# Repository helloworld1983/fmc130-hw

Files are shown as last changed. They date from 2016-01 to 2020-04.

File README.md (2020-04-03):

# FMC ADC 130M 16B 4CHA

## Project description

One of the most important goals in every light source is to achieve
orbit stability for the electron beam within the required specifications
for the stability of the photon beam in the experimental stations.
Several technical challenges make the task of achieving sub-micrometer
stability really demanding in terms of mechanical and electrical
engineering. Fast feedback systems are employed to dump orbit
distortions through accurate measurements of the beam positions, fast
computation of the corrections and actuation back to the beam through
fast power supplies and steering magnets. To realize this task in the
\*SIRIUS\*http://www.lnls.br, the new brazilian synchrotron light
source, a digital platform to measure the beam position is required.
Inside this plattaform a key part is the analog to digital conversion.
This text will describe the main specification for an FMC
Analog-to-digital conversion board.

There are several commercial off-the-shelf digitizers covering a wide
range of speed, bandwidth and resolution, but there is no board that
cover all features required for the LNLS
design.

-----



*FMC ADC 130M 16B 4CHA production board** - ([Top
view](https://www.ohwr.org/project/fmc-adc-130m-16b-4cha/uploads/23f18a16ba281e2f93acb31782c0db42/top_r.jpg), [Bottom
view](https://www.ohwr.org/project/fmc-adc-130m-16b-4cha/uploads/616fc42ba8aeb56efde3af8f24af65d3/bot_r.jpg), [Front
view](https://www.ohwr.org/project/fmc-adc-130m-16b-4cha/uploads/30c50ed58559d64d9c38bfc512450c89/fmc_bot.jpg) )

## Functional specifications

- VITA 57.1-2010 compliant
- Four Channel 16 bit 130 MSPS ADC. Required ADC: LTC2208IUP
- Internal ADC clock circuit: Phase locked to the external reference clock input with fine frequency tuning capability. See specific section. Hold mode in case of loss of external reference is a desirable feature.
- Internal high frequency PLL oscillator output with amplitude control and locked to external reference.
- External ADC clock input (50 MHz up to 130 MHz, 0 dBm typ.)
- External reference clock input: (0.5 MHz - 20 MHz digital signal, 0 dBm typ.)
- External digital Trigger input
- External digital Trigger output
-----
## Detailed project information
Block diagram

|Date|Activity|
|----|----|
|01/10/2011|First sudies about necessities|
|27/11/2011|FMC standard choosed|
|05/03/2012|Project started at OHWR|
|15/03/2012|ADC choosed|
|26/03/2012|power dissipation solutions studied|
|04/05/2012|Specification document V1.0 done|
|22/05/2012|Start of block diagram design: clock schemes, PS, input stage,FMC interface,etc|
|01/08/2012|Start collaboration with WUT/Creotech for boards design (130 and 250 MSPS versions)|
|22/10/2012|Start schematics and discussions with WUT/Creotech|
|03/12/2012|Decision of layout unification for reuse of heatsink in both boards|
|06/12/2012|Start of design modification, mechanical unification with FMC ADC 250M version|
|19/12/2012|Layout ready for review|
|21/12/2012|Fast review send from LNLS to WUT/Creotech|
|12/02/2013|Pre-assembled boards received by WUT/Creotech|
|14/02/2013|Start basic tests|
|26/04/2013|FMC ready, tested and assembled|
|30/09/2014|Available commercially|

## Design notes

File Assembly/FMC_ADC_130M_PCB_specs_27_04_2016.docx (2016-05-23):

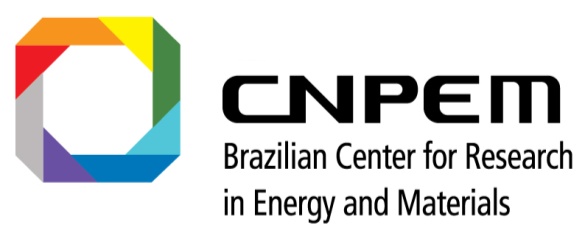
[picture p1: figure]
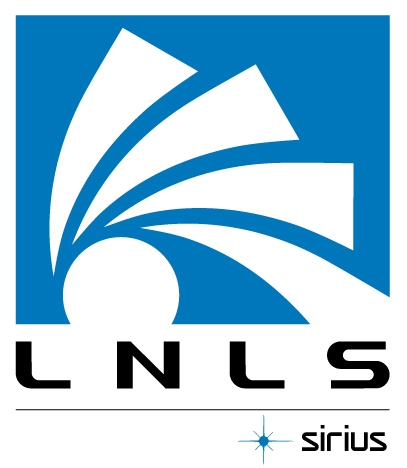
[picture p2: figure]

Manufacturing specifications for the FMC_ADC_130M hardware

April 2016

Beam Diagnostics Group (DIG)

BLANK PAGE

# PCB Fabrication Specification

Design references
Name | FMC_ADC_130M | Date: | 04/27/2015
File name
Designers | Rafael Antonio Baron | Fernando Cambauva SantAnna
E-mail | | fernando.santanna@lnls.br
Fone | | +55 19 3512-5071
Cel | | +55 16 99206-8595

Mechanical characteristics
External size (mm) | 77 x 69 mm
Thickness (mm) | 1.4 mm
Layers | 8
Min track width (mm/mils) | 3mils
Min Hole size (mm/mils) | 7.8mils
Laminate | FR-4 – TG150
Pre-preg | FR-4 – TG150

Finish Copper
External layers (µm) | 35 µm
Holes walls (µm) | 25 µm
Internal Layers-Planes (µm) | 35 µm
Internal Layers-Signals (µm) | 35 µm

Board finishing requirements
Mask Solder color | Red for prototype and Blue for production
Silkscreen on top layer (color) | White
Silkscreen on bottom layer (color) | White
Surface Finishing | ENIG – Electroless Nickel / Immersion Gold according to IPC-4552
Thickness | Ni: 3 µm min, 6 µm máx. Au: 0.05 µm min, 0.125 µm máx

Additional Information
Impedance test | No
Packaging requirements | No
Documentation to be delivered | No
Additional control quality requirements | No

| | Board Stackup Information
| Name: | | | Laminate/pre-preg | Thickness (mm/mils)
Layer 1 | Top Layer | | RF signals
Layer 2 | GND1 | | RF Ground Plane | FR-4 | 0.11mm
Layer 3 | L3 | | Digital signals | FR-4 | 0.1mm
Layer 4 | GND2 | | RF Ground Plane + Digital Ground plane | FR-4 | 0.29mm
Layer 5 | L5 | | Digital signals | FR-4 | 0.1mm
Layer 6 | GND3 | | RF Ground Plane + Digital Ground plane | FR-4 | 0.29mm
Layer 7 | Power | | Power | FR-4 | 0.1mm
Layer 8 | Bottom Layer | | Digital signals | FR-4 | 0.11mm
Total | | | | Total | 1.481 mm

Centro Nacional de Pesquisa em Energia e Materiais (CNPEM) Laboratório Nacional de Luz Síncrotron (LNLS) Rua Giuseppe Maximo Scolfaro, 10000, Polo II de Alta Tecnologia Campinas, São Paulo, Brazil CEP 13083-970 – Caixa Postal 6192

Last update: 27 April 2016 - 14:16 4

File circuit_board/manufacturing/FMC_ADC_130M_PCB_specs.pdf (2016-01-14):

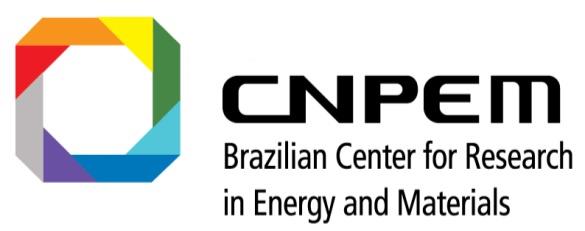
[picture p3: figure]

### Centro Nacional de Pesquisa em Energia e Materiais (CNPEM) Laboratório Nacional de Luz Síncrotron (LNLS) Rua Giuseppe Maximo Scolfaro, 10000, Polo II de Alta Tecnologia Campinas, São Paulo, Brazil CEP 13083-970 – Caixa Postal 6192

# Manufacturing specifications for the FMC_ADC_130M hardware

# December 2015

# Beam Diagnostics Group (DIG)

BLANK PAGE

Last update: 11 December 2015 - 14:26 | 3

## PCB Fabrication Specification

## Design references

Name | FMC_ADC_130M | Date: | 1/12/2015
File name
Designers | Rafael Antonio Baron | Fernando Cambauva SantAnna
E-mail | | fernando.santanna@lnls.br
Fone | | +55 19 3512-5071
Cel | | +55 19 99206-8595

## Mechanical characteristics

External size (mm) | 77 x 69 mm
Thickness (mm) | 1.4 mm
Multilayers | 6 layers
Min track width (mm/mils) | 3mils
Min Hole size (mm/mils)
Laminate | FR-4
Pre-preg | FR-4

## Finish Copper

External layers (µm) | 35 µm
Holes walls (µm) | 25 µm
Internal Layers-Planes (µm) | 35 µm
Internal Layers-Signals (µm) | 35 µm

## Board finishing requirements

Mask Solder color | Red
Silkscreen on top layer (color) | White
Silkscreen on bottom layer (color) | White
Surface Finishing | ENIG – Electroless Nickel / Immersion Gold according to IPC-4552
Thickness | Ni: 3 µm min, 6 µm máx. Au: 0.05 µm min, 0.125 µm máx

## Additional Information

Impedance test | No
Packaging requirements | No
Documentation to be delivered | No
Additional control quality requirements | No

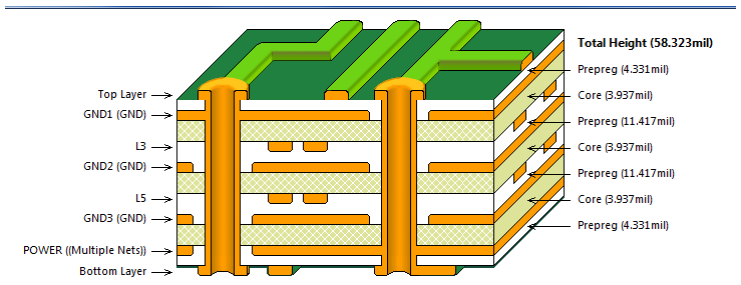
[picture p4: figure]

Last update: 11 December 2015 - 14:26 | 4

## Board Stackup Information

| | Laminate/pre-preg | Thickness (mm/mils)
Layer 1 | RF signals
Layer 2 | RF Ground Plane | FR-4 | 4.3 mils
Layer 3 | Digital signals | FR-4 | 3.9 mils
Layer 4 | RF Ground Plane + Digital Ground plane | FR-4 | 11.4 mils
Layer 5 | Digital signals | FR-4 | 3.9 mils
Layer 6 | Power | FR-4 | 4.3 mils
Total | | | 58 mils = 1.4 mm

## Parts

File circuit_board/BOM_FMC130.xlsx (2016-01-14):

BILL OF MATERIALS
Prj: | FMC - Active | REV.: 6 | Data: | 2015-11-12
QTD | Description | Manufacturer PN | Manufacturer | Designator
98 | CC0201_100NF_6.3V_10%_X5R | 02016D104KAT2A | AVX | C1A, C1B, C1C, C1D, C2A, C2B, C2C, C2D, C10, C14A, C14B, C14C, C14D, C15A, C15B, C15C, C15D, C16A, C16B, C16C, C16D, C17A, C17B, C17C, C17D, C18A, C18B, C18C, C18D, C19A, C19B, C19C, C19D, C20A, C20B, C20C, C20D, C21A, C21B, C21C, C21D, C22A, C22B, C22C, C22D, C23A, C23B, C23C, C23D, C24A, C24B, C24C, C24D, C25A, C25B, C25C, C25D, C26A, C26B, C26C, C26D, C31, C37, C39, C41, C42, C43, C44, C45, C46, C47, C48, C49, C50, C54, C59, C60, C61, C62, C63, C64, C65, C66, C67, C68, C69, C70, C71, C72, C74, C84, C103, C105, C106, C107, C108, C109, C110
4 | CC0402_1.5PF_50V_0.25PF_NP0 | 223886915158 | PHYCOMP | C5A, C5B, C5C, C5D
4 | CC0402_2.2PF_50V_0.25PF_NP0 | 223886915228 | PHYCOMP | C6A, C6B, C6C, C6D
4 | CC0603_2.2UF_16V_10%_X5R | CC0603KRX5R7BB225 | YAGEO | C12A, C12B, C12C, C12D
6 | CC1206_22UF_6.3V_20%_X5R | C1206C226K9PAC | KEMET | C27, C32, C33, C34, C81, C82
13 | CC0805_10UF_16V_10%_X5R | C0805C106K4PAC | KEMET | C28, C29, C36, C38, C51, C75, C76, C85, C86, C88, C95, C99, C100
2 | CAP. CCM SMD 330NF/50V +-10% X7R 0603 | C1608X7R1H334K | TDK | C30, C73
1 | CTE7343-31_100UF_20V_10% | TAJD107K020R | AVX | C35
7 | CC0603_1UF_25V_10%_X7R | GRM188R71E105KA12D | MURATA | C52, C79, C80, C93, C94, C98, C102
1 | CAP. CCM SMD 4,7UF/10V +-10% X5R 0603 | C0603C475K8PACTU | KEMET | C53
2 | CC0603_27NF_25V_10%_X7R | 223891615642 | PHYCOMP | C55, C56
1 | CC0603_10NF_50V_10%_X7R | 223858615636 | PHYCOMP | C57
1 | CAP. CCM SMD 470NF/25V +-20% Z5U 0603 | C1608JB1E474M080AC | TDK | C58
6 | CC0805_47UF_6.3V_20%_X5R | C0805C476M9PACTU | KEMET | C77, C78, C91, C92, C97, C101
1 | CC0402_100PF_50V_5%_NP0 | 223886915101 | PHYCOMP | C96
1 | CC0201_10NF_10V_10%_X5R | 0201ZD103KAT2A | AVX | C104
1 | Serial Diode | BAR66 | INFINEON | D1
4 | 16-Bit, 130Msps ADC | LTC2208IUP#PBF | LINEAR TECHNOLOGY | IC1A, IC1B, IC1C, IC1D
2 | Digital Temperature Sensor and Thermal Watchdog with Two-Wire Interface | LM75AIMM/NOPB | TEXAS INSTRUMENTS | IC2, IC13
1 | 1.2 GHz Clock Distribution IC, PLL Core, Dividers, Delay Adjust, Eight Outputs | AD9510BCPZ | ANALOG DEVICES | IC3
1 | 4 Way-0° 50 OHM 5 to 1000 MHz Power Splitter/Combiner | SCA-4-10+ | MINI-CIRCUITS | IC4
1 | 1.7-5.5V 64K I2C Serial EEPROM | 24AA64T-I/MC | MICROCHIP TECHNOLOGY | IC5
6 | Low Noise (3uVrms), 1A, High Voltage Low-Dropout Linear Regulator | TPS7A4700RGWT | TEXAS INSTRUMENTS | IC6, IC7, IC9, IC10, IC11, IC12
1 | 4.5V-20V To 0.6V-5V, Iout 6A DC/DC low EMI uModule | LTM4606EV#PBF | LINEAR TECHNOLOGY | IC8
1 | 4-BIT DUAL-SUPPLY BUS TRANSCEIVER | SN74AVC4T245PW | TEXAS INSTRUMENTS | IC14
4 | 20-BIT DUAL SUPPLY BUS TRANSCEIVER | SN74AVC20T245ZQLR | TEXAS INSTRUMENTS | IC15A, IC15B, IC15C, IC15D
1 | 2:1 Differential-to-LVDS Multiplexer | ICS854S015CKI-01LF | IDT, Integrated Device Technology Inc | IC16
1 | High Speed Differential Transceiver LVDS/LVTTL | SN65LVDM176DGK | TEXAS INSTRUMENTS | IC17
3 | CONN MMCX JACK R/A 50 OHM PCB | 262105 | AMPHENOL | J1, J2, J10
2 | U.FL | U.FL-R-SMT-1 | HIROSE (HRS) | J3, J4
4 | RF Connector, SMA Right Angle PCB Jack, 50 Ohm | 901-143-4 | AMPHENOL | J5, J6, J7, J8
1 | Connector VITA 57, 400 Male contacts in 10 row | ASP-134488-01 | SAMTEC | J9
5 | Inductor 0402 220ohm±25% | BLM15HB221SN1 | MURATA | L2A, L2B, L2C, L2D,L8
13 | Inductor 0805 220ohm±25% | BLM21PG221SN1D | MURATA | L3, L4A, L4B, L4C, L4D, L6, L7, L12, L13, L14A, L14B, L14C, L14D
5 | MA-COM E-Serie RF 1:1 Transmission Line Ttransformer 4.5-3000MHz | MABA-007159-000000 | MA-COM TECHNOLOGY | L1A, L1B, L1C, L1D,L5
3 | Indutor Choke Coil 2.2uH, 1.4A, 92mR ±20% | ELLVGG2R2N | Panasonic | L9, L10, L15
2 | Tricolor LEDs 1 Cathode Blue, 2 Common Anode, 3 Cathode Red, 4 Cathode Green | HSMF-C113 | AVAGO TECHNOLOGIES | LD1, LD2
1 | Any-Rate I2C Programmable XO Oscillator Si570 Serie 10-215MHZ | Si570BBC000121DG | SILICON LABS | OSC2
3 | Dual NMOS 20V,08.A, 340mR, Vt=0.7V | PMGD280UN | NXP | Q1, Q2, Q5
16 | R0402_5R6_1%_0.0625W_200PPM | RC0402FR-075R6L | YAGEO PHYCOMP | R1A, R1B, R1C, R1D, R2A, R2B, R2C, R2D, R8A, R8B, R8C, R8D, R9A, R9B, R9C, R9D
8 | R0402_33R_1%_0.0625W_100PPM | 232270673309L | YAGEO PHYCOMP | R3A, R3B, R3C, R3D, R6A, R6B, R6C, R6D
11 | R0402_10K_1%_0.0625W_100PPM | 232270671003L | YAGEO PHYCOMP | R4, R5, R10A, R10B, R10C, R10D, R32, R43, R44, R48, R80
2 | R0402_47R_1%_0.0625W_100PPM | RC0402FR-0747RL | YAGEO PHYCOMP | R7, R19
15 | R0402_200R_1%_0.0625W_100PPM | 232270672001L | YAGEO PHYCOMP | R12, R21, R25, R26, R29, R30, R31, R34, R36, R38, R52, R64, R65, R84, R85
5 | R0402_1K_1%_0.0625W_100PPM | 232270671002L | YAGEO PHYCOMP | R13A, R13B, R13C, R13D, R28
4 | R0402_2K_1%_0.0625W_100PPM | 232270672002L | YAGEO PHYCOMP | R14A, R14B, R14C, R14D
9 | R0402_100R_1%_0.0625W_100PPM | 232270671001L | YAGEO PHYCOMP | R16A, R16B, R16C, R16D, R20, R22, R75, R89,R45
12 | R0402_51R_1%_0.0625W_100PPM | 232270675109L | YAGEO PHYCOMP | R17A, R17B, R17C, R17D, R18A, R18B, R18C, R18D, R76A, R76B, R76C, R76D
25 | R0402_0R_JUMPER | 232270591001L | YAGEO PHYCOMP | R23, R27, R35, R37, R39, R40, R42, R62, R63, R66, R67, R68, R69, R70, R71, R72, R73, R77A, R77B, R77C, R77D, R86A, R86B, R86C, R86D
1 | R0402_5K1_1%_0.0625W_100PPM | RC0402FR-075K1L | YAGEO PHYCOMP | R46
1 | R0603_4K12_0.1%_0.063W_10PPM | RN73C1J4K12BTDF | TYCO HOLSWORTHY | R47
4 | R0402_2K2_1%_0.0625W_100PPM | 232270672202L | YAGEO PHYCOMP | R49, R50, R54, R55
1 | R0402_1R_1%_0.0625W_100PPM | RC0402FR-071RL | YAGEO PHYCOMP | R53
1 | R0603_4K7_1%_0.1W_100PPM | NRC06F4701TRF | NIC COMPONENT | R74
2 | R0402_100K_1%_0.0625W_100PPM | 232270671004L | YAGEO PHYCOMP | R78, R79
1 | R1210_49R9_5%_0.5W_200PPM | CRCW121049R9FKEA | Vishay Dale | R87
1 | R0402_4K7_1%_0.0625W_100PPM | 232270674702 | PHYCOMP | R88
4 | 200MHz - 500MHz Ultra Low Profile Sub-Miniature Balanced to Unbalanced Transformer | BD0205F5050A00 | ANAREN MICROWAVE | TR2, TR3, TR4, TR5
1 | 50 Ohm 0.4 To 500MHz RF Transformers | TC1-1+ | MINI-CIRCUITS | TR6

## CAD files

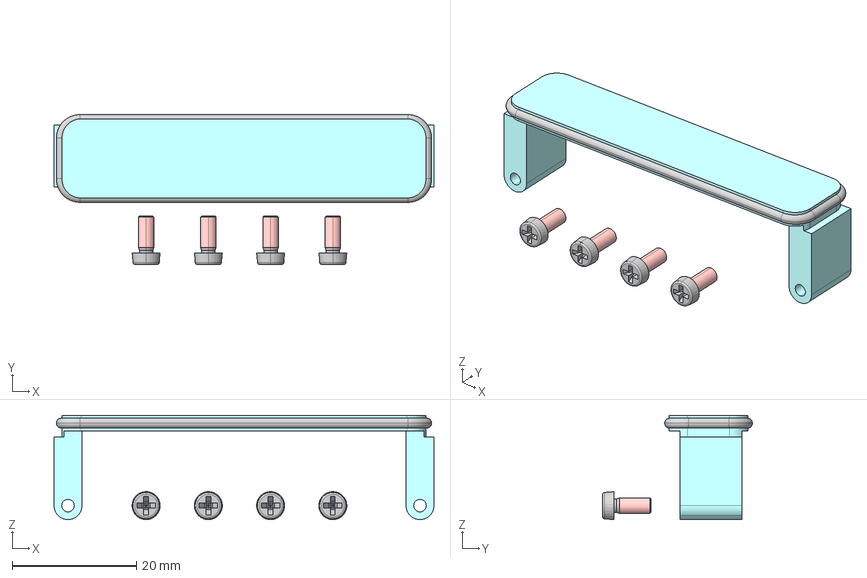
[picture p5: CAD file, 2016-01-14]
mechanical/front panel/21M280-1-3D-STEP.stp
61.0 x 24.1 x 16.8 mm
5325-06_Zylinderschraube_DCH000001699.3 x 4
61-048_EMV_Dichtung_montiert_DCH000054389
21M280_Frontplatte_DCH000054395

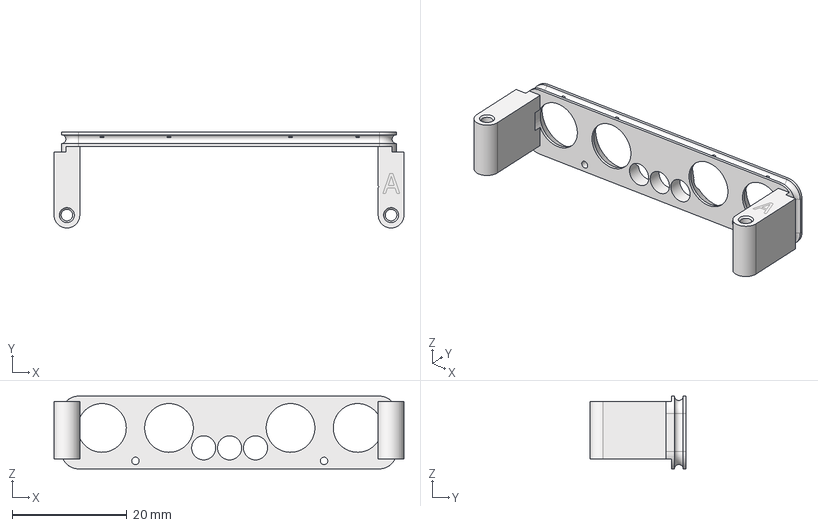
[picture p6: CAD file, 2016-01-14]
mechanical/front panel/Painel FMC v4.stp
61.1 x 16.8 x 12.7 mm

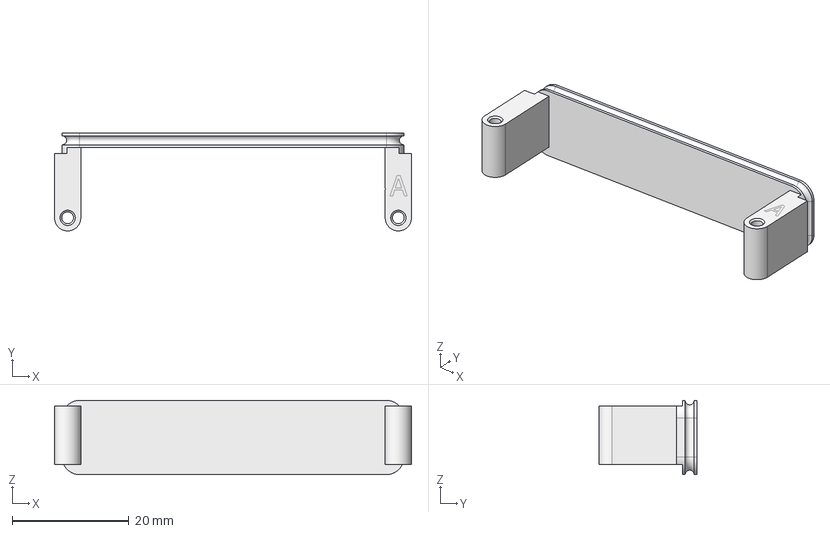
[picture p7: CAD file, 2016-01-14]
mechanical/front panel/XFM85-0001.stp
61.1 x 16.8 x 12.7 mm

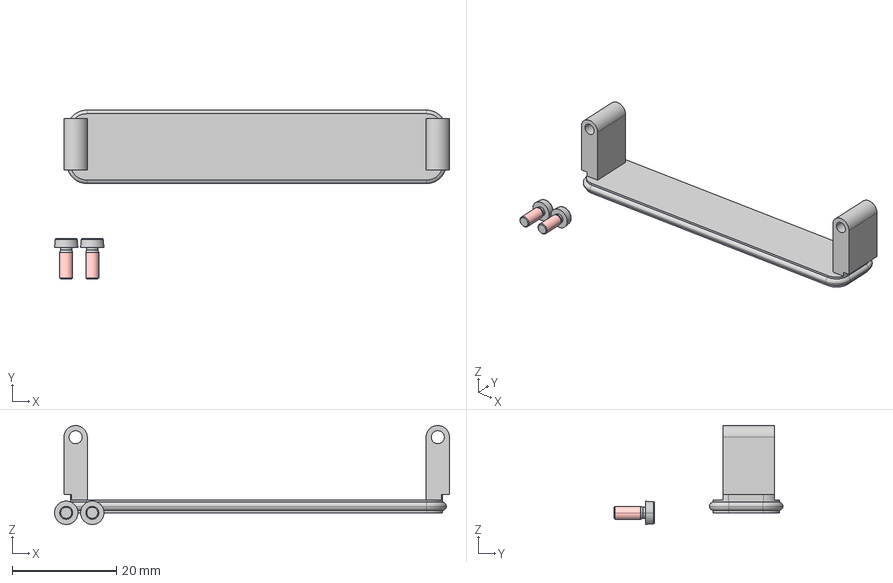
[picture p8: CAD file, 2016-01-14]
mechanical/front panel/21M271-3D-STEP.stp
75.8 x 32.4 x 19.0 mm
5325-06_Zylinderschraube_DCH000001699 x 2
21M270_Frontplatte_DCH000016520
21M570_O-Ring_DCH000016518

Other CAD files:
Mechanical/healt sink/Originais/radiator_1 (1).dwg
Mechanical/healt sink/Originais/radiator_1.dwg
mechanical/front panel/Painel FMC v4.ipt
mechanical/front panel/old_versions/Painel FMC v4.0003.ipt
mechanical/heat sink/originals/radiator_1.ipt
mechanical/heat sink/radiator_V3.ipt

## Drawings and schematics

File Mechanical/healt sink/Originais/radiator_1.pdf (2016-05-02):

30,2

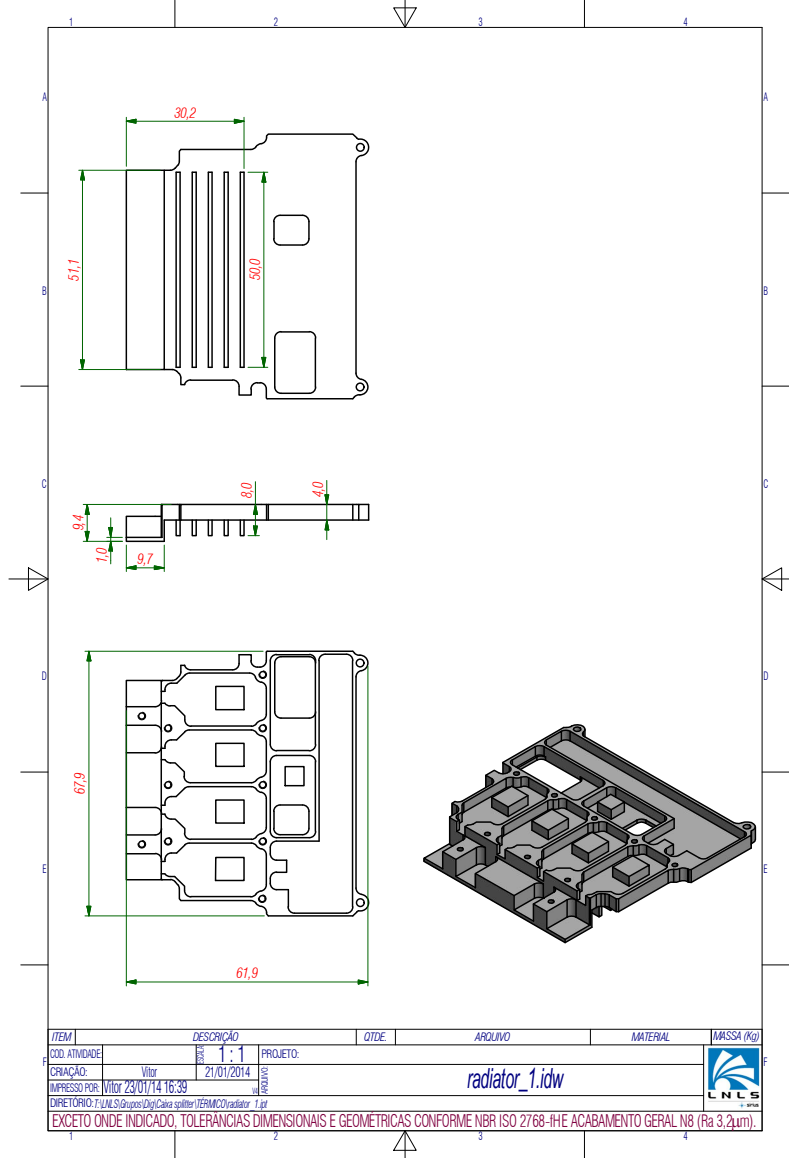
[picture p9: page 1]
ARQUIVO:; ESCALA:

ITEM | DESCRId®O | QTDE. | ARQUIVO | MATERIAL | MASSA (Kg)
COD. ATIVIDADE: | | 1 : 1 | PROJETO:
CRIAd®O: IMPRESSO POR: | Vitor | 21/01/2014 | radiator_1.idw

Vitor 23/01/14 16:39 V4

DIRETÐRIO:
EXCETO ONDE INDICADO, TOLERÇNCIAS DIMENSIONAIS E GEOMeTRICAS CONFORME NBR ISO 2768-fHE ACABAMENTO GERAL N8 (Ra 3,2Pm).

T:\LNLS\Grupos\Dig\Caixa splitter\TeRMICO\radiator_1.ipt

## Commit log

2012-11-27 Version taken from Fernando
    [ADC.SchDoc, Clock_circuit.SchDoc, EEPROM_Temp_LEDs.SchDoc, FMC connector.SchDoc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]
2012-12-14 unified shield, fixed bugs in clock distribution, unified small MOSFETs, placement done from scratch.
    [ADC.SchDoc, Clock_circuit.SchDoc, EEPROM_Temp_LEDs.SchDoc, FMC connector.SchDoc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]
2012-12-17 most of the PCB routing done - mainly FMC part missing
    [ADC.SchDoc, BUFFER.SchDoc, Clock_circuit.SchDoc, EEPROM_Temp_LEDs.SchDoc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]
2012-12-19 layout finished, only a few cosmetic cleaning required
    [ADC.SchDoc, BUFFER.SchDoc, Clock_circuit.SchDoc, EEPROM_Temp_LEDs.SchDoc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]
2013-01-07 fixed most of the issues - added 0R resistors for clock option selection, added silkscreen, logos.
    [ADC.SchDoc, BUFFER.SchDoc, Clock_circuit.SchDoc, EEPROM_Temp_LEDs.SchDoc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]
2013-01-24 added machined FMC panel, added GND layer for better copper balancing on L3, added cutouts under SMA pins and input tracks, fixed silkscreen, fixed SMA connector layout - paste and soldermask opening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
    [ADC.SchDoc, BUFFER.SchDoc, FMC_130MSPS.PrjPCB, Triggers.SchDoc]
2013-01-25 modified stackup slightly to fit to manufacturer's requirements fixed some cosmetic bugs
    [FMC_130MSPS.PrjPCB]
2013-01-31 fixed acuta angles
    [ADC.SchDoc, FMC_130MSPS.PrjPCB, power_supply.SchDoc]
2014-08-20 Added sch & pcb in pdf
    [ADC.SchDoc, BUFFER.SchDoc, Clock_circuit.SchDoc, EEPROM_Temp_LEDs.SchDoc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]
2016-01-14 New files and folders structure
    structure following the pattern DIG - mechanical missing files
    [ADC.SchDoc, BOM_FMC_v6.xlsx, BUFFER.SchDoc, Clock_circuit.SchDoc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]
2016-01-14 Add Mechanical files
    Inventor files for Panel and Heltsink
    [21M271-3D-STEP.stp, 21M280-1-3D-STEP.stp, Painel FMC v4.0003.ipt, Painel FMC v4.ipt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]
2016-01-27 Removed version from project file name
    [FMC_130MSPS.PrjPCB]
2016-02-05 reorganization of folders structure
    keep consistency wiht other Open Hardware projects
    [21M271-3D-STEP.stp, 21M280-1-3D-STEP.stp, ADC.SchDoc, BOM_FMC130.xlsx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]
2016-05-02 add new files
    [ADC.SchDoc, radiator_1 (1).dwg, radiator_1.dwg]
2016-06-08 Added schematics to project structure
    Some schematics were missing from the project structure, even though
    they were in the right directory. Edited the PrjPCB file to correct
    this.
    [FMC_130MSPS.PrjPCB]
